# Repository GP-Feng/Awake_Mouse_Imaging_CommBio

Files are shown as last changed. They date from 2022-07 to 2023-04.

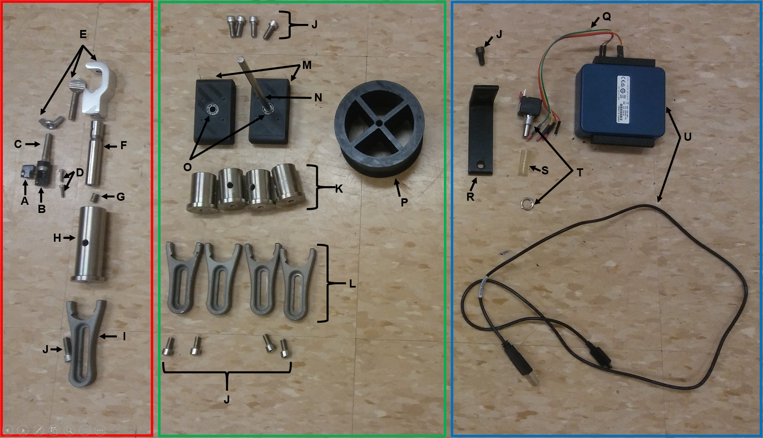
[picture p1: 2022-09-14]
Awake Mouse Setup/Assembly/Hardware _Parts_Labeled.png

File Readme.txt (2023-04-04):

Readme:
Resources and data processing codes for the paper: High-resolution structural and functional retinal imaging in the awake behaving mouse
Directories:
*.mp4: Videos instruct to assemble the head-restrained mouse setup for awake, behaving mouse retinal imaging.
\Awake_mouse_setup: Assembly instruction and 3D printing files for the head-restrained mouse setup for awake, behaving mouse retinal imaging.
\ AOSLO_linescanned_tracking: Code used to track the high-frequency eye motions from linescanned AOSLO data
\Pupil_tracking: Code used to track and segment mouse pupil
\Retina_tracking_SLO: Code used to track retinal motions from SLO videos
\OCT_segmentation: Code used to detect and segment mouse retinal layers for TRT measurement

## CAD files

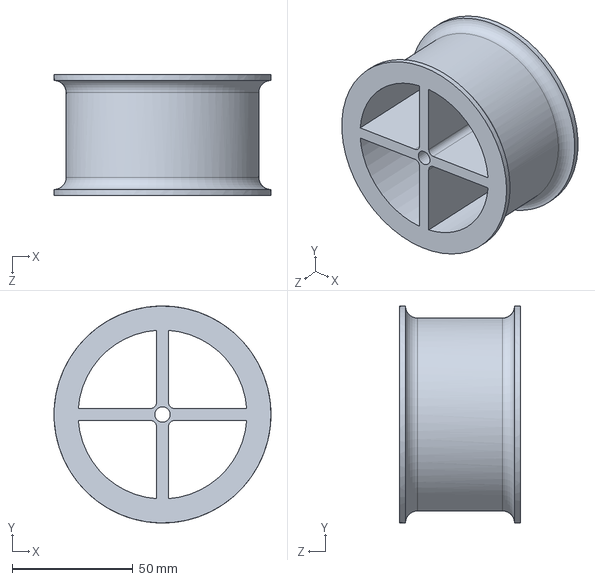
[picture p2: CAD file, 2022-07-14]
Awake Mouse Setup/3D printing files/P_SW.SLDPRT
90.0 x 90.0 x 50.0 mm

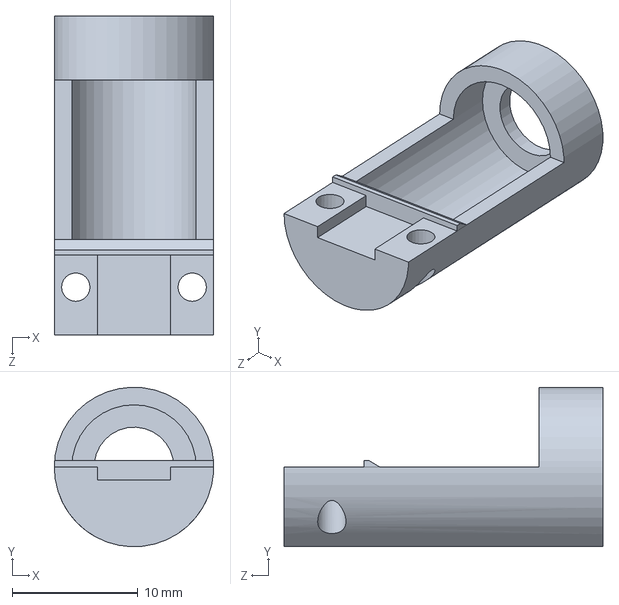
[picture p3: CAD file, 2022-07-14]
Awake Mouse Setup/3D printing files/B_SW.SLDPRT
12.7 x 12.7 x 25.4 mm

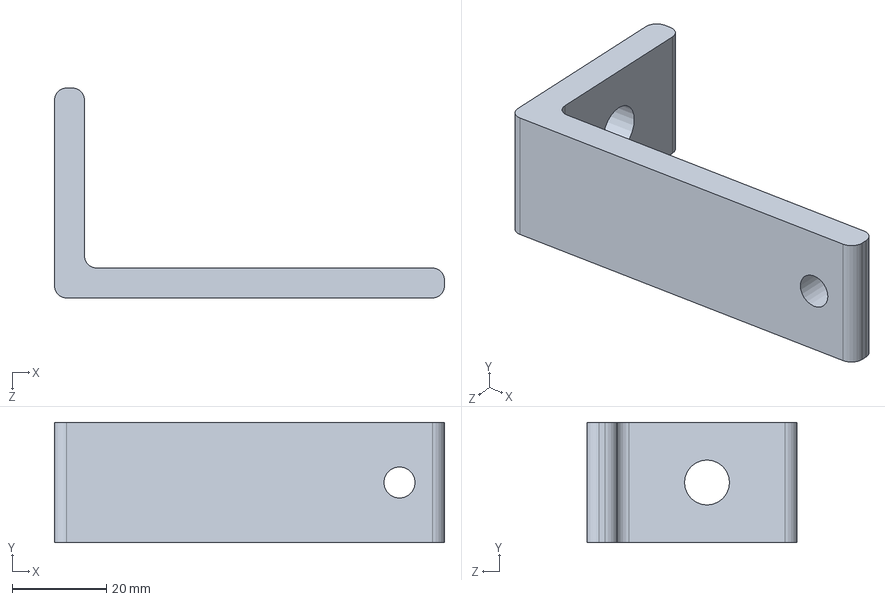
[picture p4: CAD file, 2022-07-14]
Awake Mouse Setup/3D printing files/R_SW.SLDPRT
82.5 x 25.4 x 44.5 mm

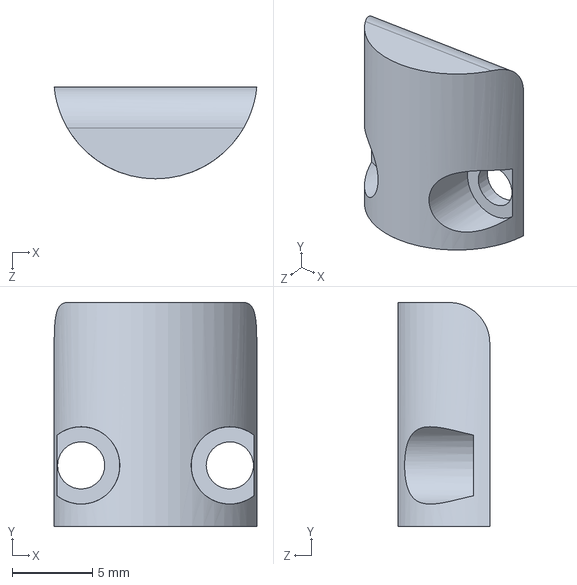
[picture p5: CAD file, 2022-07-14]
Awake Mouse Setup/3D printing files/A_SW.SLDPRT
12.6 x 14.0 x 5.72 mm

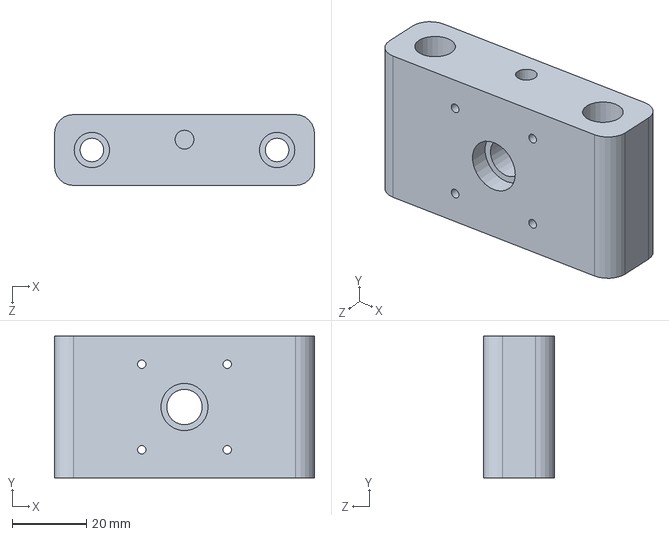
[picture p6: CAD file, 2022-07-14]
Awake Mouse Setup/3D printing files/M_SW.SLDPRT
69.8 x 38.1 x 19.1 mm

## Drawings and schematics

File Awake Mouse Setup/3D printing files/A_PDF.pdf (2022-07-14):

0 0

.07

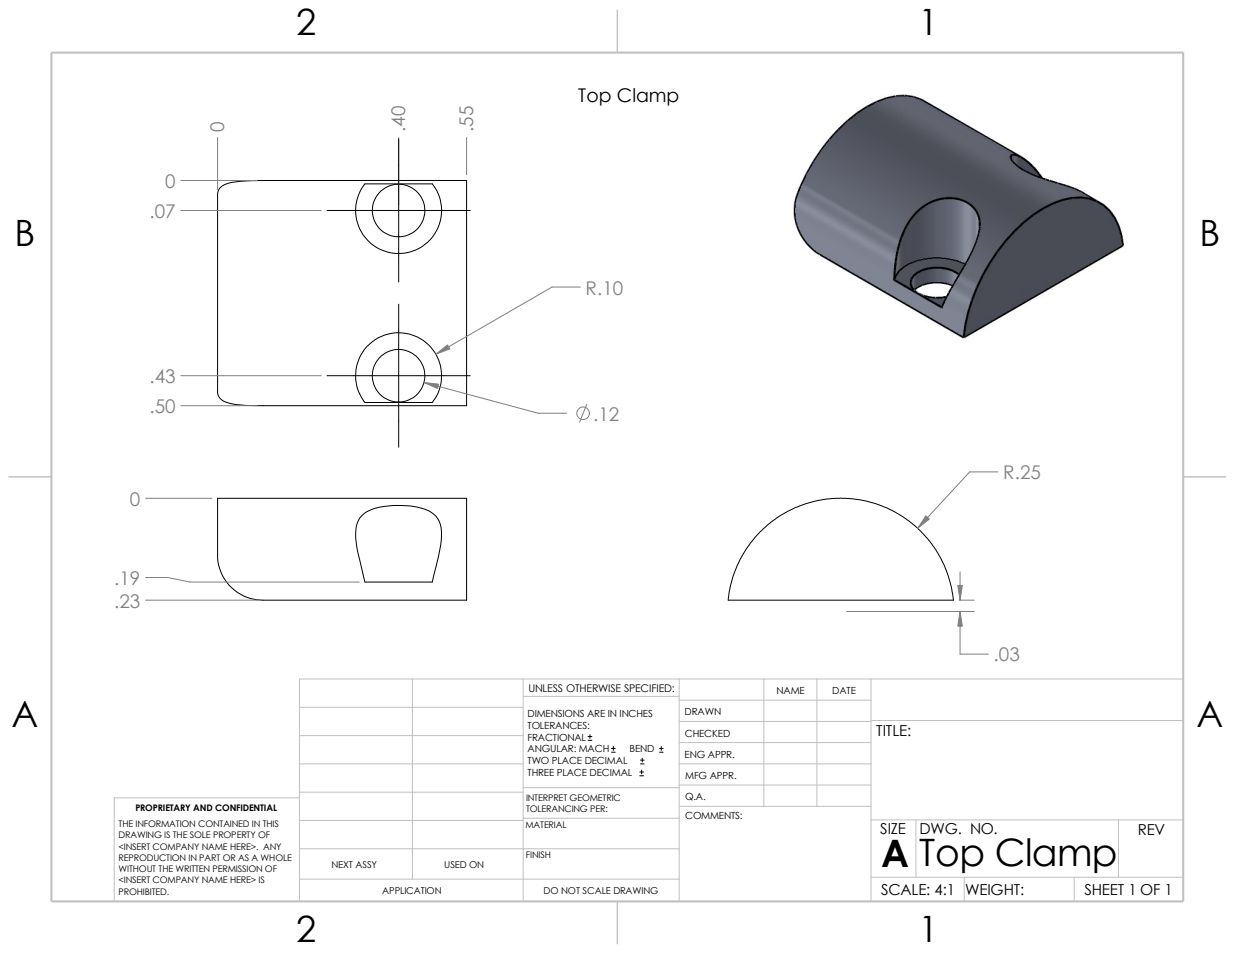
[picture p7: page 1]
Top Clamp; COMMENTS:; INTERPRET GEOMETRIC; PROPRIETARY AND CONFIDENTIAL; TOLERANCING PER:

UNLESS OTHERWISE SPECIFIED: | | NAME | DATE

DIMENSIONS ARE IN INCHES TOLERANCES: FRACTIONAL ANGULAR: MACH BEND TWO PLACE DECIMAL THREE PLACE DECIMAL | DRAWN

CHECKED | | | TITLE:

ENG APPR.
MFG APPR.

THE INFORMATION CONTAINED IN THIS
DRAWING IS THE SOLE PROPERTY OF
<INSERT COMPANY NAME HERE>. ANY
REPRODUCTION IN PART OR AS A WHOLE
WITHOUT THE WRITTEN PERMISSION OF
<INSERT COMPANY NAME HERE> IS
PROHIBITED.

MATERIAL | | SIZE A | DWG. NO. Top Clamp | REV

NEXT ASSY | USED ON | FINISH
APPLICATION | DO NOT SCALE DRAWING | | SCALE: 4:1 | WEIGHT: | SHEET 1 OF 1

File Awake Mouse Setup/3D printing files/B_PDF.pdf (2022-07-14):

.50 ⁰

1.00 .43 .50

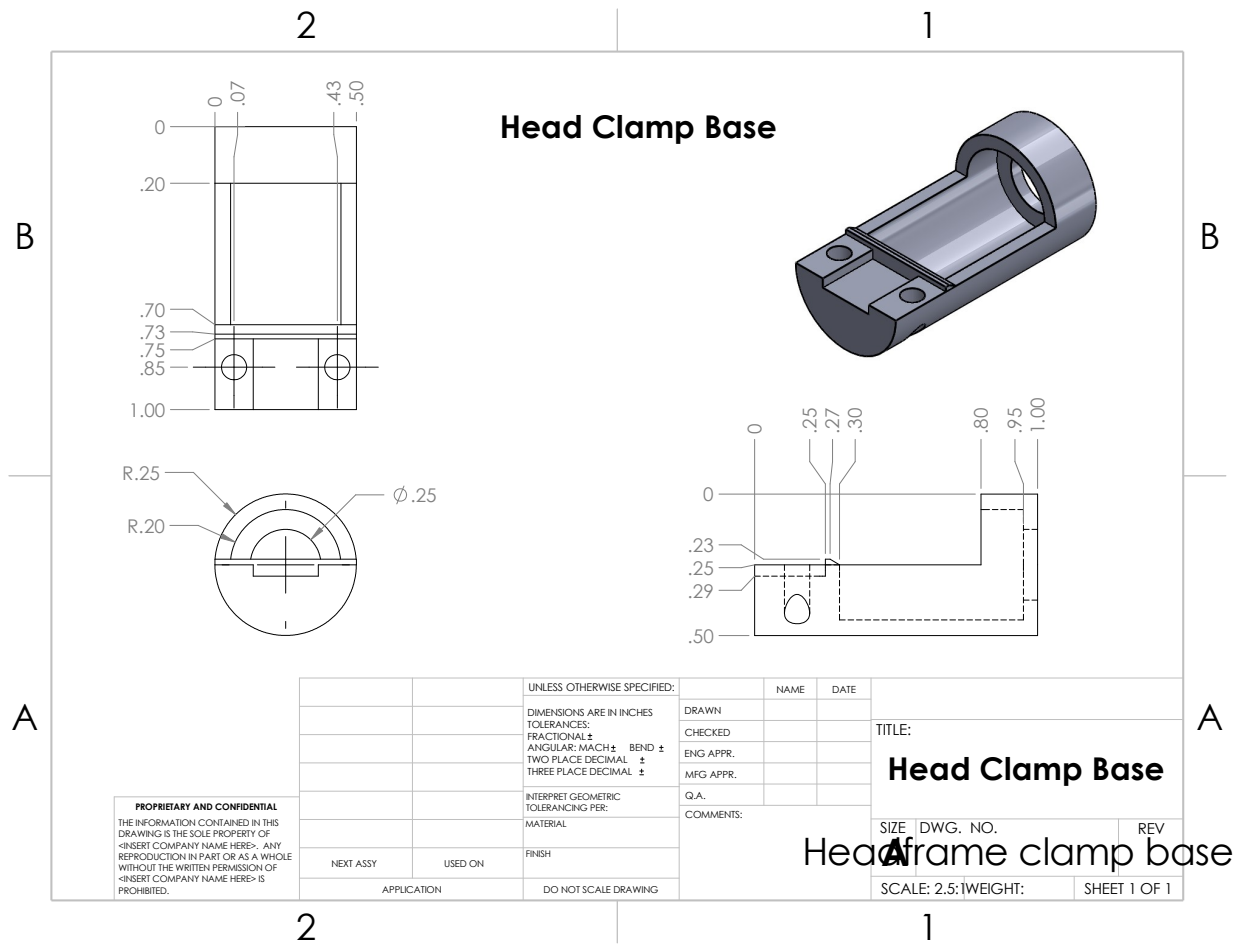
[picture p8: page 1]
Headframe clamp base; COMMENTS:

Head Clamp Base

UNLESS OTHERWISE SPECIFIED: | | NAME | DATE

DIMENSIONS ARE IN INCHES TOLERANCES: FRACTIONAL ANGULAR: MACH BEND TWO PLACE DECIMAL THREE PLACE DECIMAL | DRAWN

CHECKED | | | TITLE: Head Clamp Base

ENG APPR.
MFG APPR.

INTERPRET GEOMETRIC TOLERANCING PER: | Q.A.
MATERIAL | | SIZE A | DWG. NO. | REV

PROPRIETARY AND CONFIDENTIAL
THE INFORMATION CONTAINED IN THIS
DRAWING IS THE SOLE PROPERTY OF
<INSERT COMPANY NAME HERE>. ANY
REPRODUCTION IN PART OR AS A WHOLE
WITHOUT THE WRITTEN PERMISSION OF
<INSERT COMPANY NAME HERE> IS
PROHIBITED.

NEXT ASSY | USED ON | FINISH
APPLICATION | DO NOT SCALE DRAWING | | SCALE: 2.5:1WEIGHT: | | SHEET 1 OF 1

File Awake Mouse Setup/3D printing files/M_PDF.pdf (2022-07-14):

0 0

.27

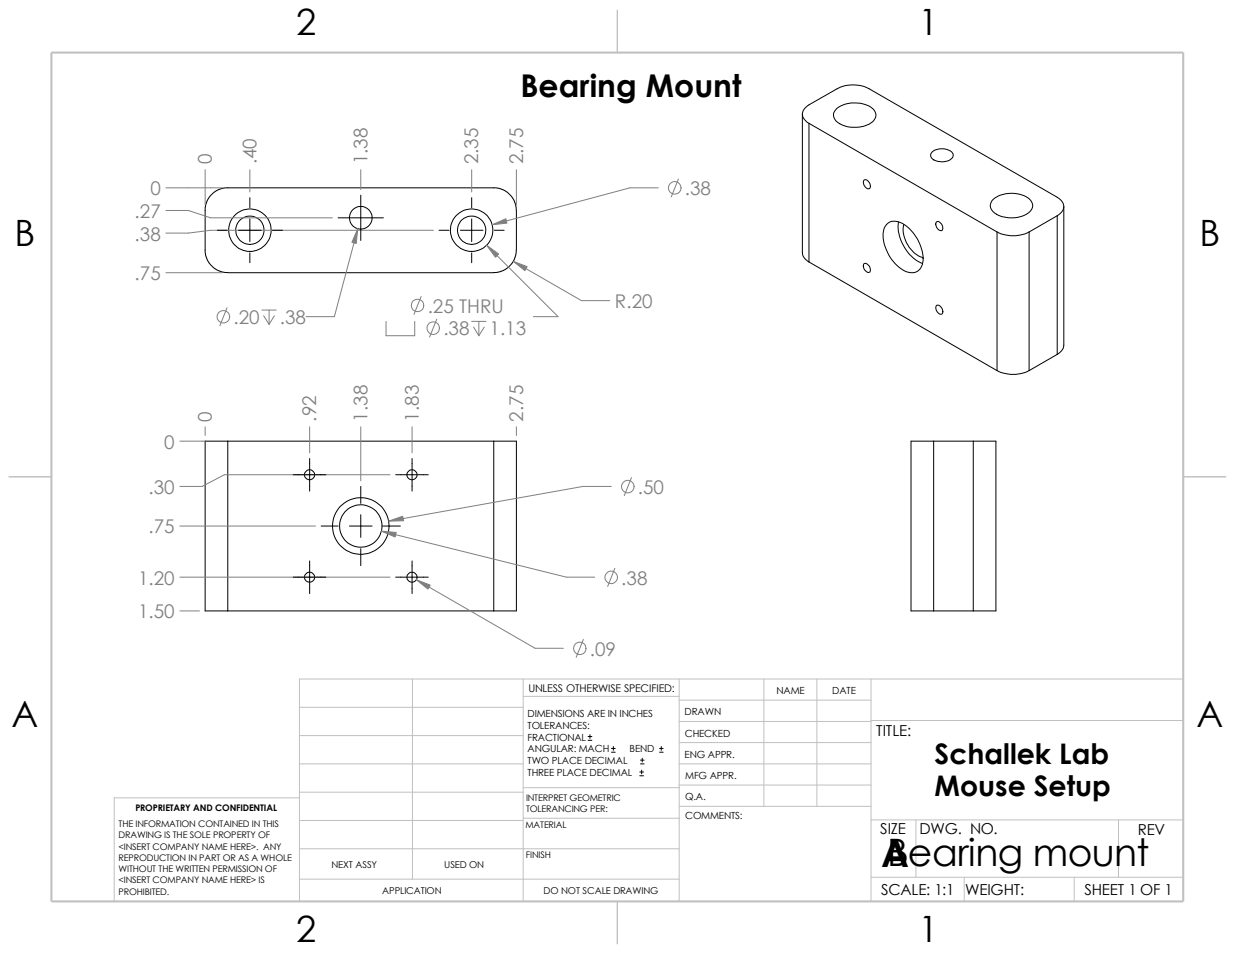
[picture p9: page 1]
COMMENTS:; INTERPRET GEOMETRIC; PROPRIETARY AND CONFIDENTIAL; TOLERANCING PER:; Bearing Mount; .25 THRU

UNLESS OTHERWISE SPECIFIED: | | NAME | DATE

DIMENSIONS ARE IN INCHES TOLERANCES: FRACTIONAL ANGULAR: MACH BEND TWO PLACE DECIMAL THREE PLACE DECIMAL | DRAWN

CHECKED | | | TITLE: Schallek Lab Mouse Setup

ENG APPR.
MFG APPR.

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

MATERIAL | | SIZE A Bearing mount | DWG. NO. | REV

NEXT ASSY | USED ON | FINISH
APPLICATION | DO NOT SCALE DRAWING | | SCALE: 1:1 | WEIGHT: | SHEET 1 OF 1

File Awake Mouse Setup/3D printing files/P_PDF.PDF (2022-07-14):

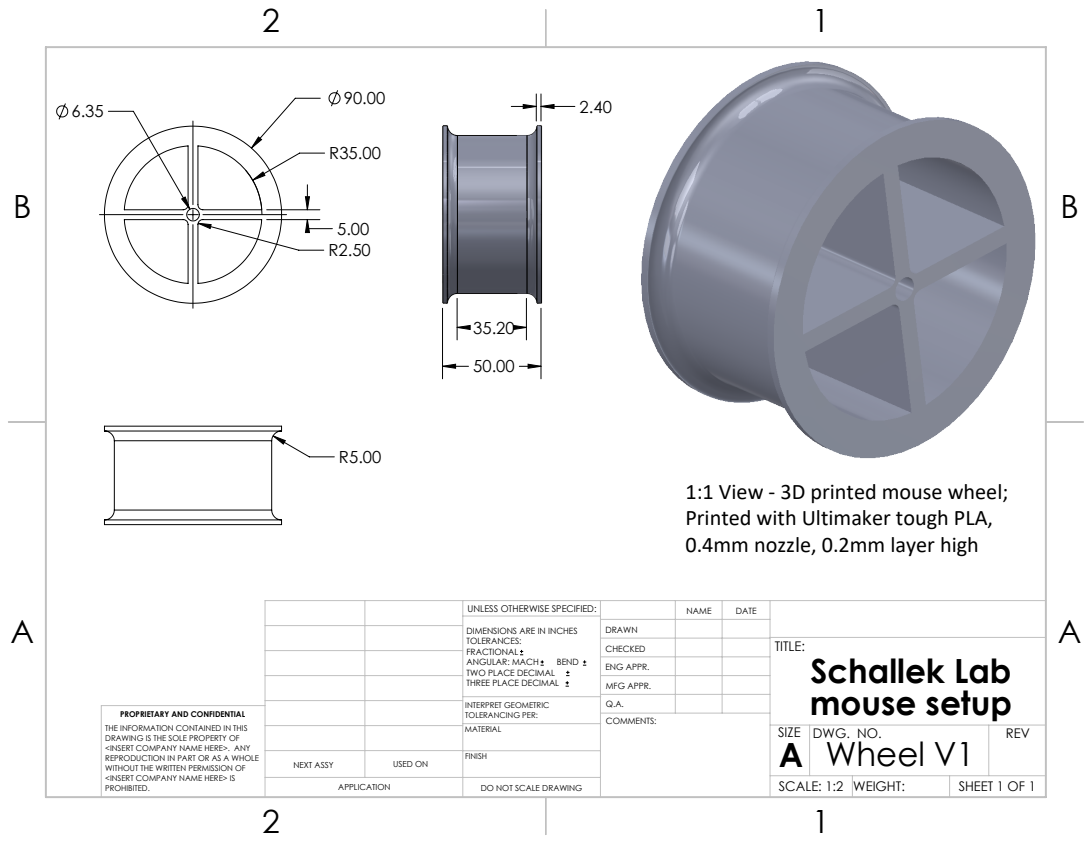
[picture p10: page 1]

1:1 View - 3D printed mouse wheel;
Printed with Ultimaker tough PLA,
0.4mm nozzle, 0.2mm layer high

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

ENG APPR.
MFG APPR.

INTERPRET GEOMETRIC TOLERANCING PER: | Q.A.
MATERIAL | | SIZE A | DWG. NO. Wheel V1 | REV

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

NEXT ASSY | USED ON | FINISH

APPLICATION | DO NOT SCALE DRAWING | | SCALE: 1:2 | WEIGHT: | SHEET 1 OF 1

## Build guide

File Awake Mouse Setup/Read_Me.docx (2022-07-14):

This folder contains the hardware and software components and setup instructions for our awake mouse imaging.

Hardware

- Pdfs and SolidWorks part/assembly files of the 3d printed components of our awake mouse set up
- Image of all hardware parts disassembled (Assembly Folder: Hardware_Parts_Labeled.png)
- Image of encoder to DAQ wiring connection (Assembly Folder: Encoder_DAQ_Wiring_Diagram.png)
- 4 assembly videos and 1 assembly document (Assembly Folder)
  - 1 for head clamp (Assembly_Video_Head_Clamp.mp4)
  - 1 for mouse wheel (Assembly_Video_Mouse_Wheel.mp4)
  - 1 for encoder (Assembly_Video_Rotary_Encoder.mp4)
  - 1 to combine all parts into the complete setup (Assembly_Video_Setup.mp4)
  - 1 instructions list (Assembly_Instructions.docx)
- Chart below that outlines each part. Red, green, and blue colored background corresponds with red, green, and blue colored outlines in Assembly Folder: Hardware_Parts_Labeled.png.

Software (ReadMouseWheel Folder)

- National Instruments software
- MATLAB files
  - load_wheel_data
  - process_wheel_data

Instructions

1. Ensure Encoder and DAQ are properly connected (see: Assembly Folder: Encoder_DAQ_Wiring_Diagram.png)
2. Ensure DAQ is plugged into the computer used for acquisition
3. Open ReadDigPort
4. Click start prior to data collection and stop after data collection
5. Move resulting .DAT file to appropriate folder location if not already
6. Read .DAT file into MATLAB process_wheel_data

Name | PDF | SolidWorks | Model || Company | Cost Est. | Note
A Head Clamp (Top)* | A_PDF | A_SW | 3D printed | N/A | Clamp to mouse headplate
B Head Clamp (Bottom)* | B_PDF | B_SW | 3D printed | N/A | Clamp to mouse headplate
C Screw | N/A | N/A | SH6MS35 || THORLLABS Newton, NY, USA (https://www.thorlabs.com/newgrouppage9.cfm?objectgroup_id=5894) | $13 for 25 pack | Hold head clamp
D Screw (2x) | N/A | N/A | SH3M10 || THORLABS, NJ, USA (https://www.thorlabs.com/newgrouppage9.cfm?objectgroup_id=5894) | $9 for 50 pack | Used to tighten head clamp
E Burette Clamp | N/A | N/A | CE-CLAMP || HomeScienceTools (https://www.homesciencetools.com/product/burette-clamp/?nosto=nosto-page-category1) | $7 | Hold head clamp. Does not have to be this exact clip. Unscrew test tube clamp so head clamp can go in its place
F Mini-Series Post | ** | ** | MS3R/M || THORLABS, NJ, USA (https://www.thorlabs.com/newgrouppage9.cfm?objectgroup_id=1257) | $9 | Part of head clamp stand
G Setscrew | N/A | N/A | AE4E25E || THORLABS, NJ, USA (https://www.thorlabs.com/newgrouppage9.cfm?objectgroup_id=1257) | $5 | Secure pillar post to pedestal
H Pedestal Pillar Post | ** | ** | RS3P8E || THORLABS Newton, NJ, USA (https://www.thorlabs.com/newgrouppage9.cfm?objectgroup_id=851) | $29 | Part of head clamp stand
I Clamping Fork | ** | ** | CF175 || THORLABS Newton, NJ, USA (https://www.thorlabs.com/newgrouppage9.cfm?objectgroup_id=887) | $11 | Hold head clamp pedestal in place
J Screw (10x) | N/A | N/A | SH4MS16 || THORLABS Newton, NJ, USA (https://www.thorlabs.com/newgrouppage9.cfm?objectgroup_id=5894) | $28 | Used to secure clamping forks, bearing mount, L-bracket
K Pedestal Pillar Post (4x) | ** | ** | RS1.5P8E || THORLABS Newton, NJ, USA (https://www.thorlabs.com/newgrouppage9.cfm?objectgroup_id=851) | $100 | Part of mouse wheel holder; align with holes in bearing mount
L Clamping Fork (4x) | ** | ** | CF125 || THORLABS Newton, NJ, USA (https://www.thorlabs.com/newgrouppage9.cfm?objectgroup_id=887) | $37 | Holds mouse wheel pedestals in place
M Bearing Mount (2x)* | M_PDF | M_SW | 3D printed | N/A | Part of mouse wheel holder
N Assembly Rod | ** | ** | ER8 || THORLABS Newton, NJ, USA (https://www.thorlabs.com/newgrouppage9.cfm?objectgroup_id=4125) | $12 | Part of mouse wheel axel
O Steel Ball Bearing (2x) | N/A | N/A | R188 || McMaster-Carr Elmhurst, IL, USA (https://www.mcmaster.com/57155K356/) | $13 | Part of mouse wheel axel
P Mouse Wheel* | P_PDF | P_SW | 3D printed | N/A | Mouse wheel
Q Breadboard Jumper Wires | N/A | N/A | EDGELEC Guangdong, China (https://www.amazon.com/EDGELEC-Breadboard-Optional-Assorted-Multicolored/dp/B07GD2BWPY) | $6 | Connects encoder to DAQ Board
R L-Bracket* | R_PDF | R_SW | 3D printed | N/A | Holds encoder to end of axel
S Polyurethane Tube | N/A | N/A | 5108K52 || McMaster-Carr Elmhurst, IL, USA (https://www.mcmaster.com/5108K52/) | $2 | Connects encoder to axel
T Rotary Encoder | N/A | N/A | ENS1J-B28 L00256L || Bourns, Inc. Riverside, CA, USA (https://www.digikey.at/product-detail/en/bourns-inc/ENS1J-B28-L00256L/ENS1J-B28-L00256L-ND/1089392) | $58 | Encoder to detect rotation
U DAQ Board | N/A | N/A | USB-6001 || National Instruments Austin, TX, USA (https://www.ni.com/en-us/support/model.usb-6001.html) | $220 | Collects encoder information and connects to computer
Breadboard | N/A | N/A | Variable || THORLABS Newton, NJ, USA (https://www.thorlabs.com/navigation.cfm?guide_id=40) | Variable | Holds entire setup
Tough PLA | N/A | N/A | Ultimaker B.V. ED Utrecht, Netherlands (https://ultimaker.com/materials/tough-pla) | $50 per 2.85mm (750g) | 3D printing material

Estimated Total Cost: $559 (if all THORLABS parts are bought) plus printing cost. **Any THORLAB component can be 3D printed from the files provided on their site if this is a more economical choice.

*We 3D printed all parts with Ultimaker S5 printer and CURA to slice models using specific settings:

- 0.4mm diameter nozzle
- 0.2mm layer height
- 50% infill
- Wall line count = 4
- No support
- The rest of the slicer settings were unchanged from CURA’s default for Tough PLA.

Notes: Solidworks files may have limited use/functionality in other CAD programs.

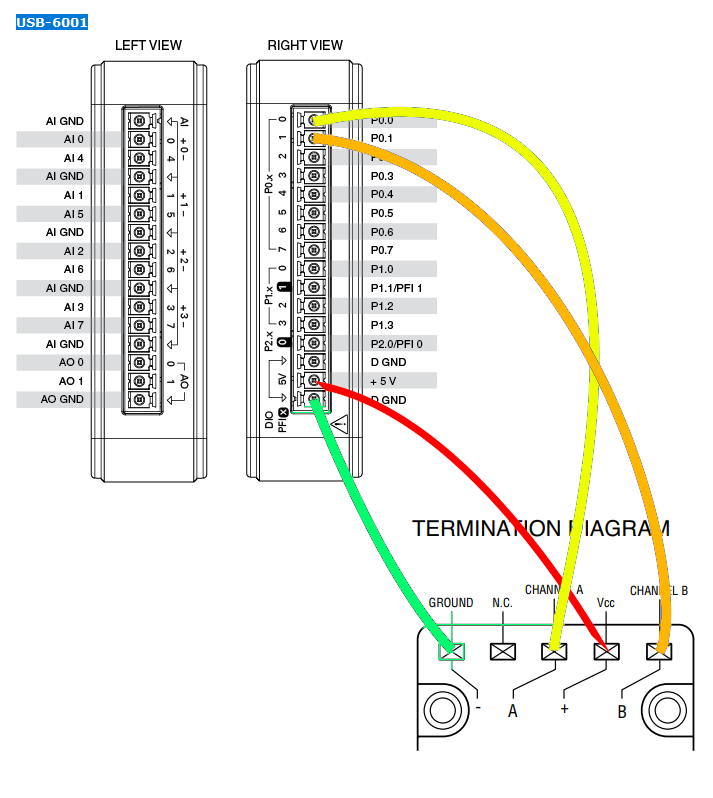
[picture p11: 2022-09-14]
Awake Mouse Setup/Assembly/Encoder_DAQ_Wiring_Diagram.png
